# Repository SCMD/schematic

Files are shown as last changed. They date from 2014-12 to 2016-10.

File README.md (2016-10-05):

## SCMD-2 PCB

SCMD-2 design source, schematic and PCB layout.

PDF exports of the schematics, layout and BOM are located in [export](/export)
directory. Deisgn files are located in the root directiry of the repo. To
access the design files you need KiCAD installed.

Make sure that PCU meets EN60601-1 and EN55011 Class B (approved for medical
use). We use widely available [Cincon TR30RAM180](https://www.cincon.com/productdownload/Datasheet-TR30RAM.pdf).

For firmware used with this project navigate [here](https://github.com/SCMD/firmware).

## License

Copyright (C) 2014, Centre for Decision Research and Experimental Economics
(CeDEx), the University of Nottingham.

This documentation describes Open Hardware and is licensed under the CERN OHL
v. 1.2.  You may redistribute and modify this documentation under the terms of
the CERN OHL v.1.2. (http://ohwr.org/cernohl). This documentation is
distributed WITHOUT ANY EXPRESS OR IMPLIED WARRANTY, INCLUDING OF
MERCHANTABILITY, SATISFACTORY QUALITY AND FITNESS FOR A PARTICULAR PURPOSE.
Please see the CERN OHL v.1.2 for applicable conditions

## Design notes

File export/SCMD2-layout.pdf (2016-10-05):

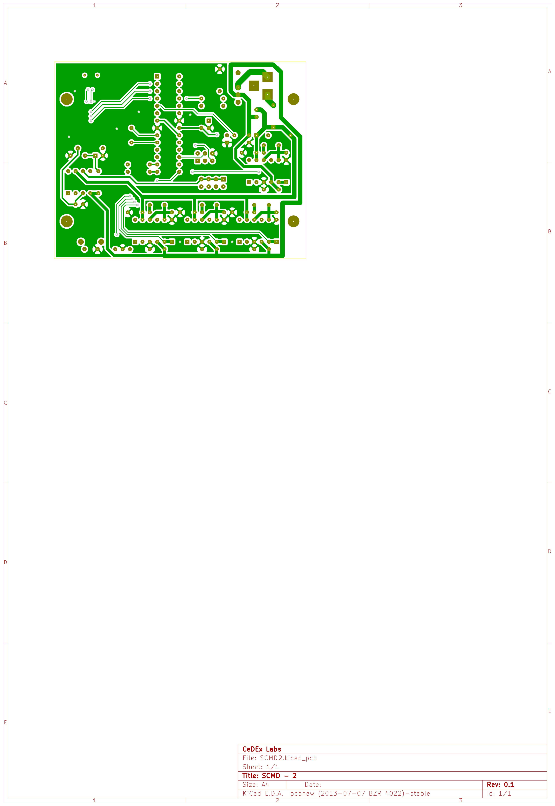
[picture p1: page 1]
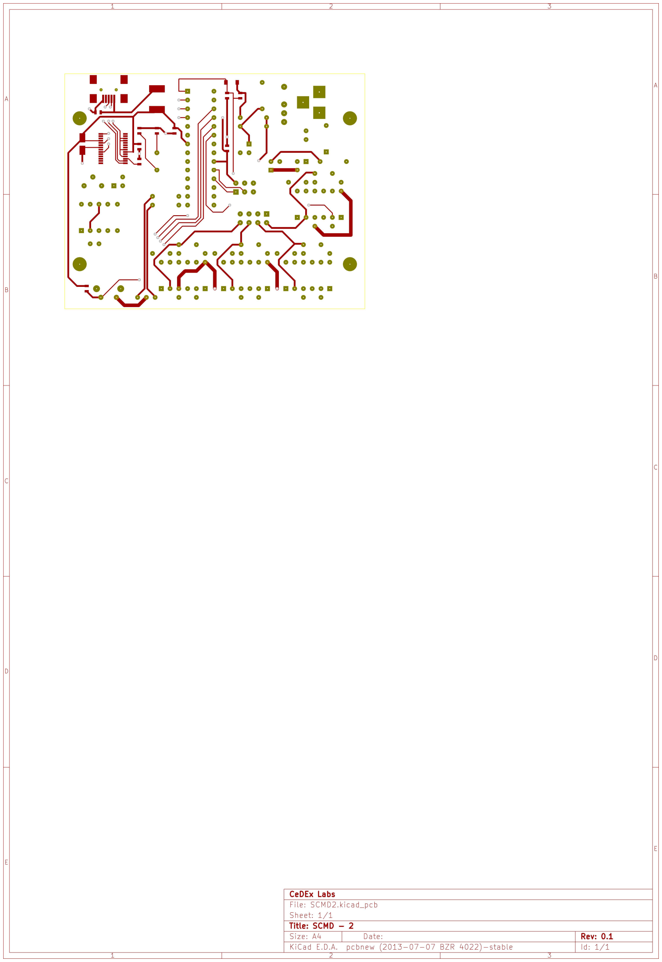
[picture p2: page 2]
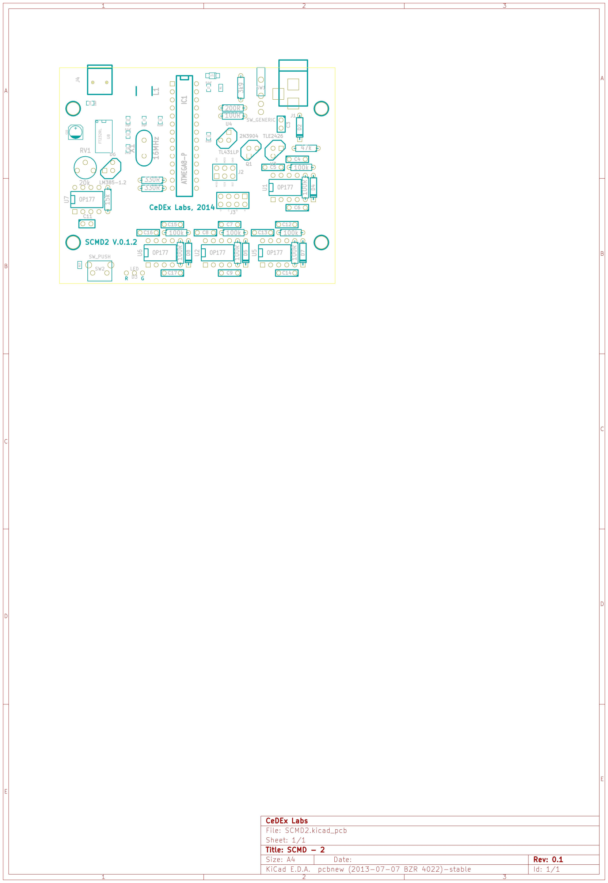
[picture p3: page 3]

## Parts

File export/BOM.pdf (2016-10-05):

SCMD-2 BOM | v0.1.2
Id | Designator | Package | Quantity | Designation | Ref | Supplier
1 J4 | USB_MINI_B | 1 MINIUSB | 2059755 uk.farnell.com
2 U4 | TO92 | 1 TL431LP | 9593543 uk.farnell.com
3 U3 | TO92 | 1 TLE2426 | 1207287 uk.farnell.com
4 Q1 | TO92 | 1 2N3904 | 1574370 uk.farnell.com
5 SW1 | SW_M7RE | 1 SW_GENERIC | 1550095 uk.farnell.com
6 U8 | SSOP28 | 1 FT232RL | 1146032 uk.farnell.com
7 C18 | SM0603_Capa | 1 10nF | 2280646 uk.farnell.com
8 C10,C2 | SM0603_Capa | 2 22pF | 2332610 uk.farnell.com
9 C19,C23,C1,C20,C21 SM0603_Capa | 5 0.1uF | 2332664 uk.farnell.com
10 R1,R17 | SM0603 | 2 10k | 2331740 uk.farnell.com
11 L1 | self_cms_we-tpc_XL | 1 100uH | 2333942 uk.farnell.com
12 RV1 | RV2 | 1 20k | 108251 uk.farnell.com
13 R14,R13,R2,R3 | R3 | 4 100k | 2329606 uk.farnell.com
R11 | R3 | 1 100R | 2329854 uk.farnell.com
14 R16,R5,R15,R6 | R3 | 4 100R | 2329607 uk.farnell.com
15 R9 | R3 | 1 200R | 2330059 uk.farnell.com
16 R7,R8 | R3 | 2 330R | 2329663 uk.farnell.com
17 R12 | R3 | 1 3k9 | 9341854 uk.farnell.com
18 R4 | R3 | 1 47k | 2329681 uk.farnell.com
19 R10 | R3 | 1 15k | 2329619 uk.farnell.com
| 20 SW2 | pushbutton_side | | 1 SW_PUSH
21 J3 | pin_array_4x2 | 1 SKIN_EL | 3417827 uk.farnell.com
22 J2 | pin_array_3x2 | 1 ICSP | 3417827 uk.farnell.com
23 X1 | HC-49V | 1 16MHz | 1640875 uk.farnell.com
24 U5,U7,U2,U6,U1 | DIP-8__300 | 5 OP177 | 9604685 uk.farnell.com
25 IC1 | DIP-28__300 | 1 ATMEGA8-P | 1715487 uk.farnell.com
26 D4,D5,D7,D8 | D3 | 4 1N4734A | 1861448 uk.farnell.com
27 C22 | c_elec_4x5.3 | 1 10uF | 2326109 uk.farnell.com
28 C16,C17,C5,C6,C9,C8,C14,C13 C2 | 8 0.1uF | 2395773 uk.farnell.com
29 C4,C15,C12,C7 | C2 | 4 1.5uF | 1869990 uk.farnell.com
| 30 C11 | C1 | | 1 10uF
31 J1 | BARREL_JACK | 1 PWR JACK | 224959 uk.farnell.com
32 D6 | TO92-123 | 1 LM385-1.2 | 9488430 uk.farnell.com
33 D2 | D3 | 1 1N4001 | 1651089 uk.farnell.com
34 D1 | SOD-123 | 1 1n4148 | 1621821 uk.farnell.com
35 C3 | C1 | 1 220uF | 2346579 uk.farnell.com
36 D3 | double_led | 1 LED | 1142520 uk.farnell.com

* SM mounted components are marked in yellow

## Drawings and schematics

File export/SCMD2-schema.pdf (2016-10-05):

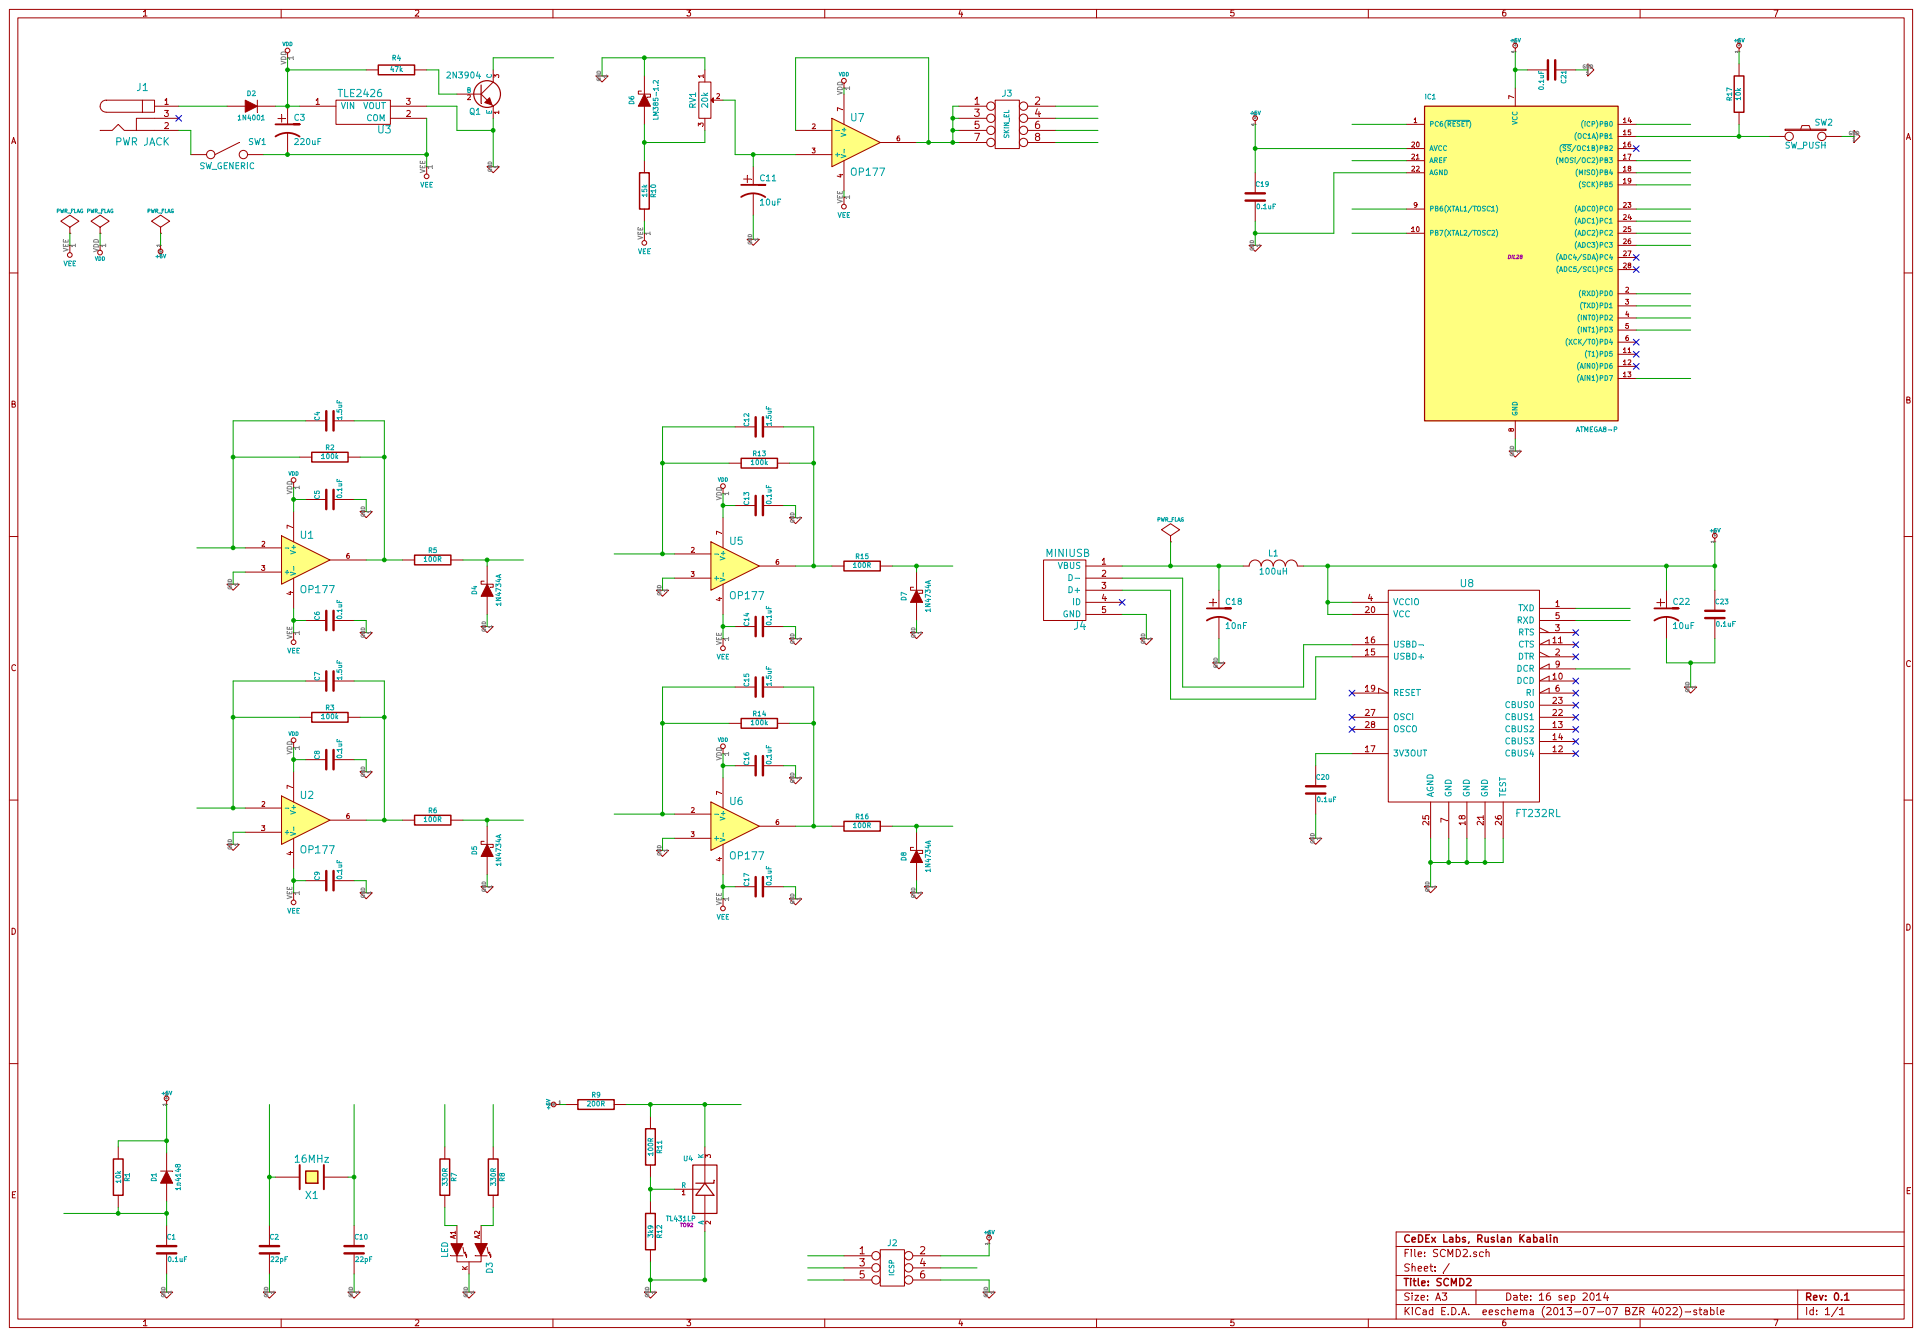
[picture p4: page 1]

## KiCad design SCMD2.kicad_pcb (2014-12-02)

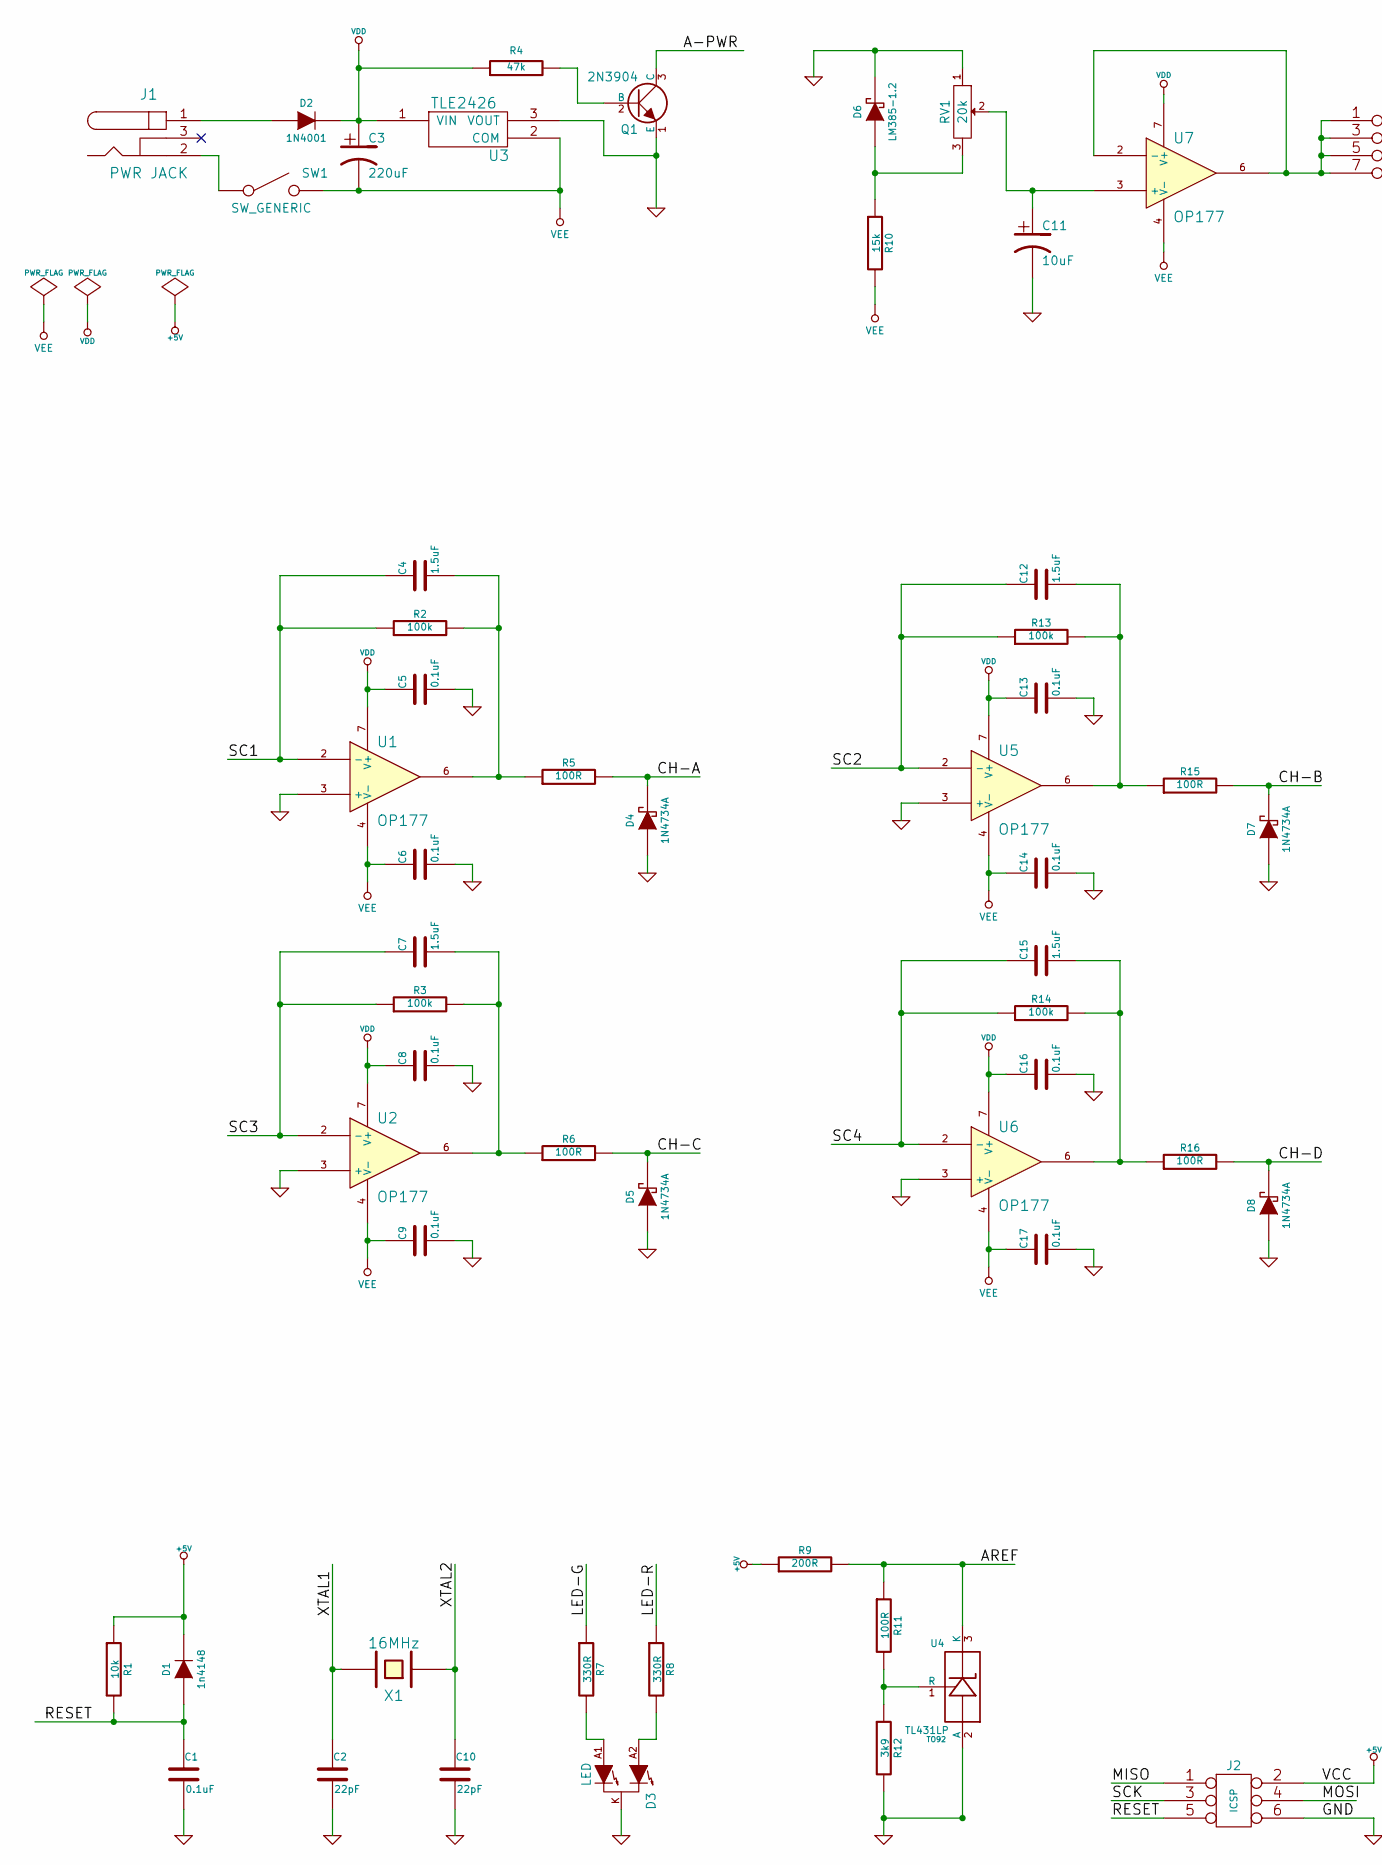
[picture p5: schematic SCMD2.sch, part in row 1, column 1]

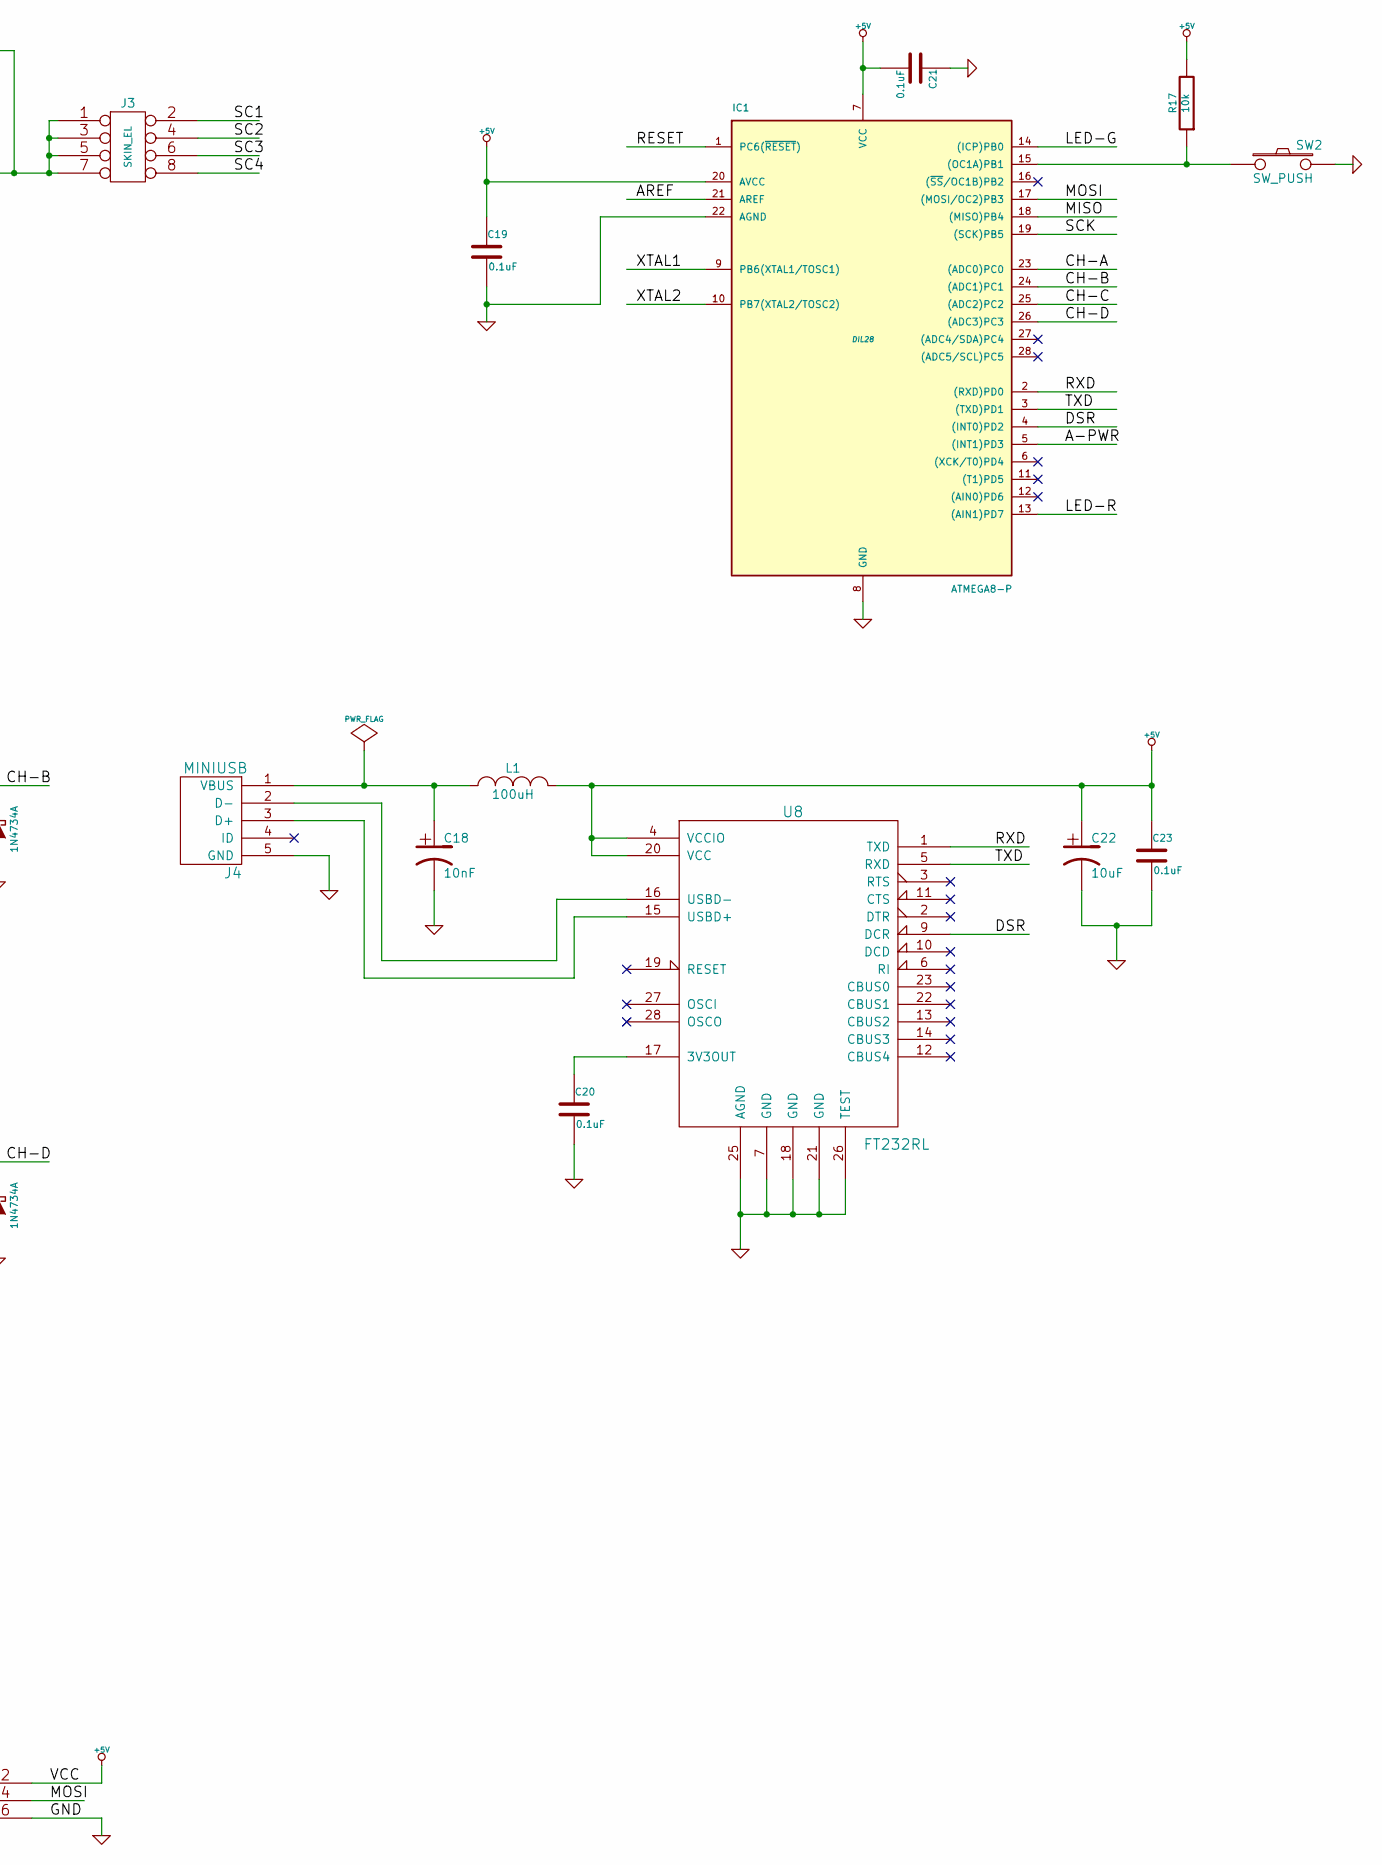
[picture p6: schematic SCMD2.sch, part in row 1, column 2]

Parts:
C1, C5, C6, C8, C9, C13, C14, C16, C17, C19, C20, C21, C23: 0.1uF
C2, C10: 22pF
C3: 220uF
C4, C7, C12, C15: 1.5uF
C11, C22: 10uF
C18: 10nF
D1: 1n4148
D2: 1N4001
D3: LED
D4, D5, D7, D8: 1N4734A
D6: LM385-1.2
IC1: ATMEGA8-P; DIL28
J1: PWR JACK
J2: ICSP
J3: SKIN_EL
J4: MINIUSB
L1: 100uH
Q1: 2N3904
R1, R17: 10k
R2, R3, R13, R14: 100k
R4: 47k
R5, R6, R11, R15, R16: 100R
R7, R8: 330R
R9: 200R
R10: 15k
R12: 3k9
RV1: 20k
SW1: SW_GENERIC
SW2: SW_PUSH
U1, U2, U5, U6, U7: OP177
U3: TLE2426
U4: TL431LP; TO92
U8: FT232RL
X1: 16MHz

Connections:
+5V: C19.1, C21.2, C22.1, C23.1, D1.2 (K), IC1.7 (VCC), IC1.20 (AVCC), J2.2, L1.2, R1.1, R9.1, R17.2, U8.4 (VCCIO), U8.20 (VCC)
/A-PWR: IC1.5 ((INT1)PD3), Q1.3 (C)
/AREF: IC1.21 (AREF), R9.2, R11.1, U4.3 (K)
/CH-A: D4.2 (K), IC1.23 ((ADC0)PC0), R5.2
/CH-B: D7.2 (K), IC1.24 ((ADC1)PC1), R15.2
/CH-C: D5.2 (K), IC1.25 ((ADC2)PC2), R6.2
/CH-D: D8.2 (K), IC1.26 ((ADC3)PC3), R16.2
/DSR: IC1.4 ((INT0)PD2), U8.9 (DCR)
/LED-G: IC1.14 ((ICP)PB0), R7.1
/LED-R: IC1.13 ((AIN1)PD7), R8.1
/MISO: IC1.18 ((MISO)PB4), J2.1
/MOSI: IC1.17 ((MOSI/OC2)PB3), J2.4
/RESET: C1.1, D1.1 (A), IC1.1 (PC6(~RESET~)), J2.5, R1.2
/RXD: IC1.2 ((RXD)PD0), U8.1 (TXD)
/SC1: C4.1, J3.2, R2.1, U1.2 (-)
/SC2: C12.1, J3.4, R13.1, U5.2 (-)
/SC3: C7.1, J3.6, R3.1, U2.2 (-)
/SC4: C15.1, J3.8, R14.1, U6.2 (-)
/SCK: IC1.19 ((SCK)PB5), J2.3
/TXD: IC1.3 ((TXD)PD1), U8.5 (RXD)
/XTAL1: C2.1, IC1.9 (PB6(XTAL1/TOSC1)), X1.2
/XTAL2: C10.1, IC1.10 (PB7(XTAL2/TOSC2)), X1.1
GND: C1.2, C2.2, C5.2, C6.2, C8.2, C9.2, C10.2, C11.2, C13.2, C14.2, C16.2, C17.2, C18.2, C19.2, C20.2, C21.1, C22.2, C23.2, D3.K, D4.1 (A), D5.1 (A), D6.2 (K), D7.1 (A), D8.1 (A), IC1.8 (GND), IC1.22 (AGND), J2.6, J4.5 (GND), Q1.1 (E), R12.2, RV1.1, SW2.2, U1.3 (+), U2.3 (+), U3.3 (VOUT), U4.2 (A), U5.3 (+), U6.3 (+), U8.7 (GND), U8.18 (GND), U8.21 (GND), U8.25 (AGND), U8.26 (TEST)
unnamed: C12.2, R13.2, R15.1, U5.6
unnamed: C15.2, R14.2, R16.1, U6.6
unnamed: C4.2, R2.2, R5.1, U1.6
unnamed: C20.1, U8.17 (3V3OUT)
unnamed: J1.2, SW1.1
unnamed: C18.1, J4.1 (VBUS), L1.1
unnamed: J4.2 (D-), U8.16 (USBD-)
unnamed: J4.3 (D+), U8.15 (USBD+)
unnamed: R11.2, R12.1, U4.1 (R)
unnamed: D3.A1, R7.2
unnamed: D3.A2, R8.2
unnamed: D2.1 (A), J1.1
unnamed: IC1.15 ((OC1A)PB1), R17.1, SW2.1
unnamed: J3.1, J3.3, J3.5, J3.7, U7.2 (-), U7.6
unnamed: C7.2, R3.2, R6.1, U2.6
unnamed: C11.1, RV1.2, U7.3 (+)
unnamed: D6.1 (A), R10.1, RV1.3
unnamed: Q1.2 (B), R4.2
VDD: C3.1, C5.1, C8.1, C13.1, C16.1, D2.2 (K), R4.1, U1.7 (V+), U2.7 (V+), U3.1 (VIN), U5.7 (V+), U6.7 (V+), U7.7 (V+)
VEE: C3.2, C6.1, C9.1, C14.1, C17.1, R10.2, SW1.2, U1.4 (V-), U2.4 (V-), U3.2 (COM), U5.4 (V-), U6.4 (V-), U7.4 (V-)

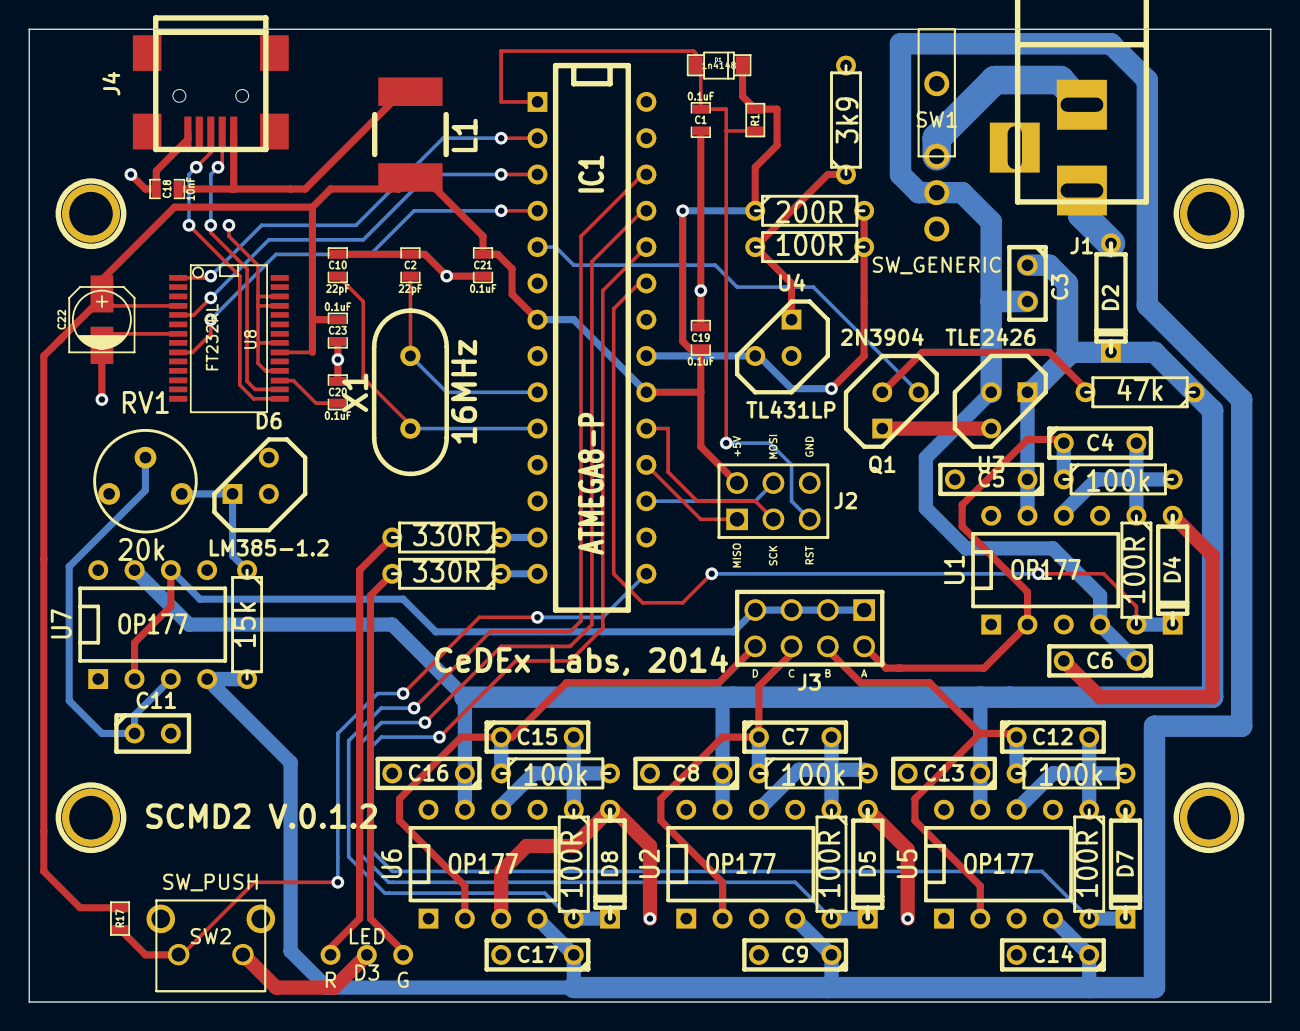
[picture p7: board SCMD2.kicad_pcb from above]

Board: 2 copper layers, 86.9 x 68.1 mm, 71 parts (0 on the bottom side), 43 nets.

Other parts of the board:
1PIN, 1PIN#2, 1PIN#3, 1PIN#4: P***; 1pin

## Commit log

2014-10-16 Initial commit.
    [SCMD2.kicad_pcb, SCMD2.sch]
2014-10-16 Add filling zone and connect GND.
    [SCMD2.kicad_pcb]
2014-10-22 Add board info.
    [SCMD2.kicad_pcb]
2014-10-24 Fix mini-usb mod and improve ground filling connectivity.
    [SCMD2.kicad_pcb]
2014-12-02 Refactor PCB and release SCMD2 V.0.1.2
    * Fix L1 footprint,
    * Refactor tracks to avoid their accidential damage,
    * Replace TO92 footprints to match case type,
    * Use SM0603 for R1,
    * Add pin labels for J2 and J3,
    * Add D3 LED labels,
    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
    [SCMD2-B_Cu.gbl, SCMD2-B_Mask.gbs, SCMD2-B_Paste.gbp, SCMD2-B_SilkS.gbo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]
